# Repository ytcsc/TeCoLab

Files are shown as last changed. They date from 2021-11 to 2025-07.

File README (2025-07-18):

TeCoLab stands for Temperature Control Laboratory. It is an open source platform that contains (Arduino Nano compatible) hardware, firmware (Arduino Nano) and software (Python). The purpose of this project is to provide a cheap platform to help any interested person to understand several basic concepts about control systems. This project uses a MIT License, which means that you are basically free to do anything you like with this project.

All documentation has been moved to the (Wiki)[https://github.com/ytcsc/TeCoLab/wiki]!

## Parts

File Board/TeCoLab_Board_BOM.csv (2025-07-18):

Reference | Value | Footprint | Datasheet | Qty | DNP
A1 | Arduino_Nano_v3.x | Module:Arduino_Nano | http://www.mouser.com/pdfdocs/Gravitech_Arduino_Nano3_0.pdf | 1
C1 | 220uF x 25 V | Capacitor_THT:CP_Radial_D8.0mm_P3.50mm | ~ | 1
C2,C3,C4,C5 | 100nF | Capacitor_THT:C_Rect_L7.0mm_W2.0mm_P5.00mm | ~ | 4
D1,D2 | LED | LED_THT:LED_D3.0mm | ~ | 2
D3,D4 | 1N4007 | Diode_THT:D_DO-41_SOD81_P10.16mm_Horizontal | http://www.vishay.com/docs/88503/1n4001.pdf | 2
H1,H2,H3,H4,H5,H6,H7,H8 | Hole | MountingHole:MountingHole_3.2mm_M3,MountingHole:MountingHole_6mm | ~ | 8
J1 | Jack | Connector_BarrelJack:BarrelJack_Horizontal | ~ | 1
J2 | Supply_Terminal | TerminalBlock:TerminalBlock_bornier-2_P5.08mm | ~ | 1
J3 | DC Cooler | TerminalBlock:TerminalBlock_bornier-2_P5.08mm | ~ | 1
Q1 | BC337 | Package_TO_SOT_THT:TO-92_HandSolder | https://diotec.com/tl_files/diotec/files/pdf/datasheets/bc337.pdf | 1
Q2,Q3 | TIP122 | Package_TO_SOT_THT:TO-220-3_Vertical | http://www.fairchildsemi.com/ds/TI/TIP120.pdf | 2
R1,R2,R11,R13 | 1K | Resistor_THT:R_Axial_DIN0207_L6.3mm_D2.5mm_P7.62mm_Horizontal | ~ | 4
R3,R5,R7,R8 | 4.7K | Resistor_THT:R_Axial_DIN0207_L6.3mm_D2.5mm_P7.62mm_Horizontal | ~ | 4
R4,R9,R10 | 330R | Resistor_THT:R_Axial_DIN0207_L6.3mm_D2.5mm_P7.62mm_Horizontal | ~ | 3
R6,R12,R14 | 1K8 | Resistor_THT:R_Axial_DIN0207_L6.3mm_D2.5mm_P7.62mm_Horizontal | ~ | 3
R15,R16,R17,R18 | 10R / 5W | Resistor_THT:R_Axial_DIN0617_L17.0mm_D6.0mm_P20.32mm_Horizontal | ~ | 4
TP1,TP2,TP3,TP4,TP5,TP6,TP7,TP8 | TestPoint | TestPoint:TestPoint_THTPad_D1.0mm_Drill0.5mm | ~ | 8
U1,U3,U4 | DS18B20 | Package_TO_SOT_THT:TO-92_HandSolder | http://datasheets.maximintegrated.com/en/ds/DS18B20.pdf | 3
U2,U5,U6 | PC817 | Package_DIP:DIP-4_W7.62mm | http://www.soselectronic.cz/a_info/resource/d/pc817.pdf | 3

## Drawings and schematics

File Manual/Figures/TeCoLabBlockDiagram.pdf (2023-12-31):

## tecolab.py

# Arduino Nano

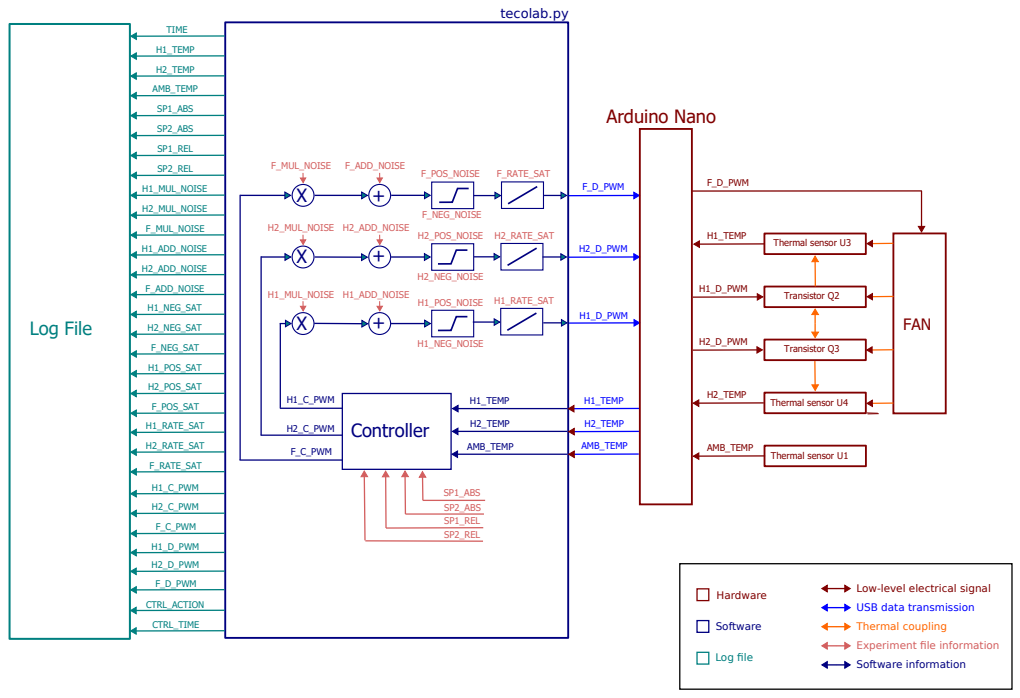
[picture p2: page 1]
H1_TEMP; H2_TEMP; AMB_TEMP; F_D_PWM; H2_D_PWM; H1_D_PWM; Thermal sensor U3; Transistor Q2; Transistor Q3; Thermal sensor U4; Thermal sensor U1; TIME; SP2_ABS; SP1_ABS; CTRL_ACTION; F_C_PWM; H2_C_PWM; H1_C_PWM; F_POS_SAT; H2_POS_SAT; H1_POS_SAT; F_NEG_SAT; H2_NEG_SAT; H1_NEG_SAT; F_ADD_NOISE; H2_ADD_NOISE; H1_ADD_NOISE; F_MUL_NOISE; H2_MUL_NOISE; H1_MUL_NOISE; SP2_REL; SP1_REL; H1_MUL_NOISE H1_ADD_NOISE H1_POS_NOISE; H1_NEG_NOISE; H2_MUL_NOISE H2_ADD_NOISE; H2_POS_NOISE; H2_NEG_NOISE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

Low-level electrical signal
USB data transmission
Thermal coupling
Experiment file information
Software information

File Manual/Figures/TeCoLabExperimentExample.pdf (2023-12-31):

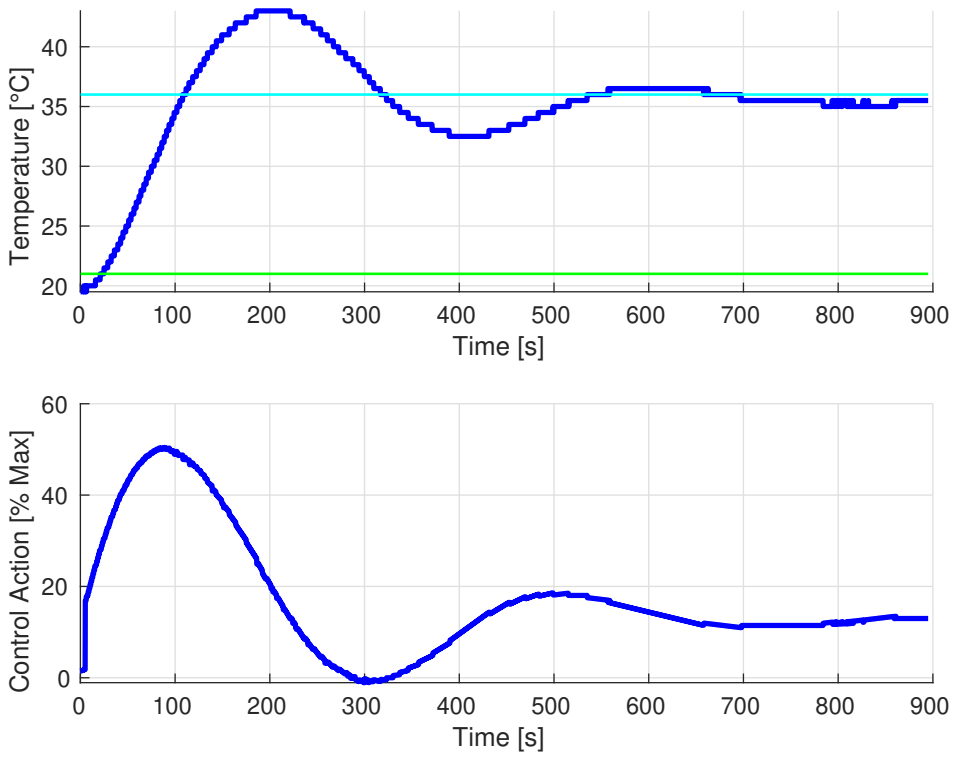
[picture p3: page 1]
Time [s]; Temperature [°C]

Control Action [% Max]

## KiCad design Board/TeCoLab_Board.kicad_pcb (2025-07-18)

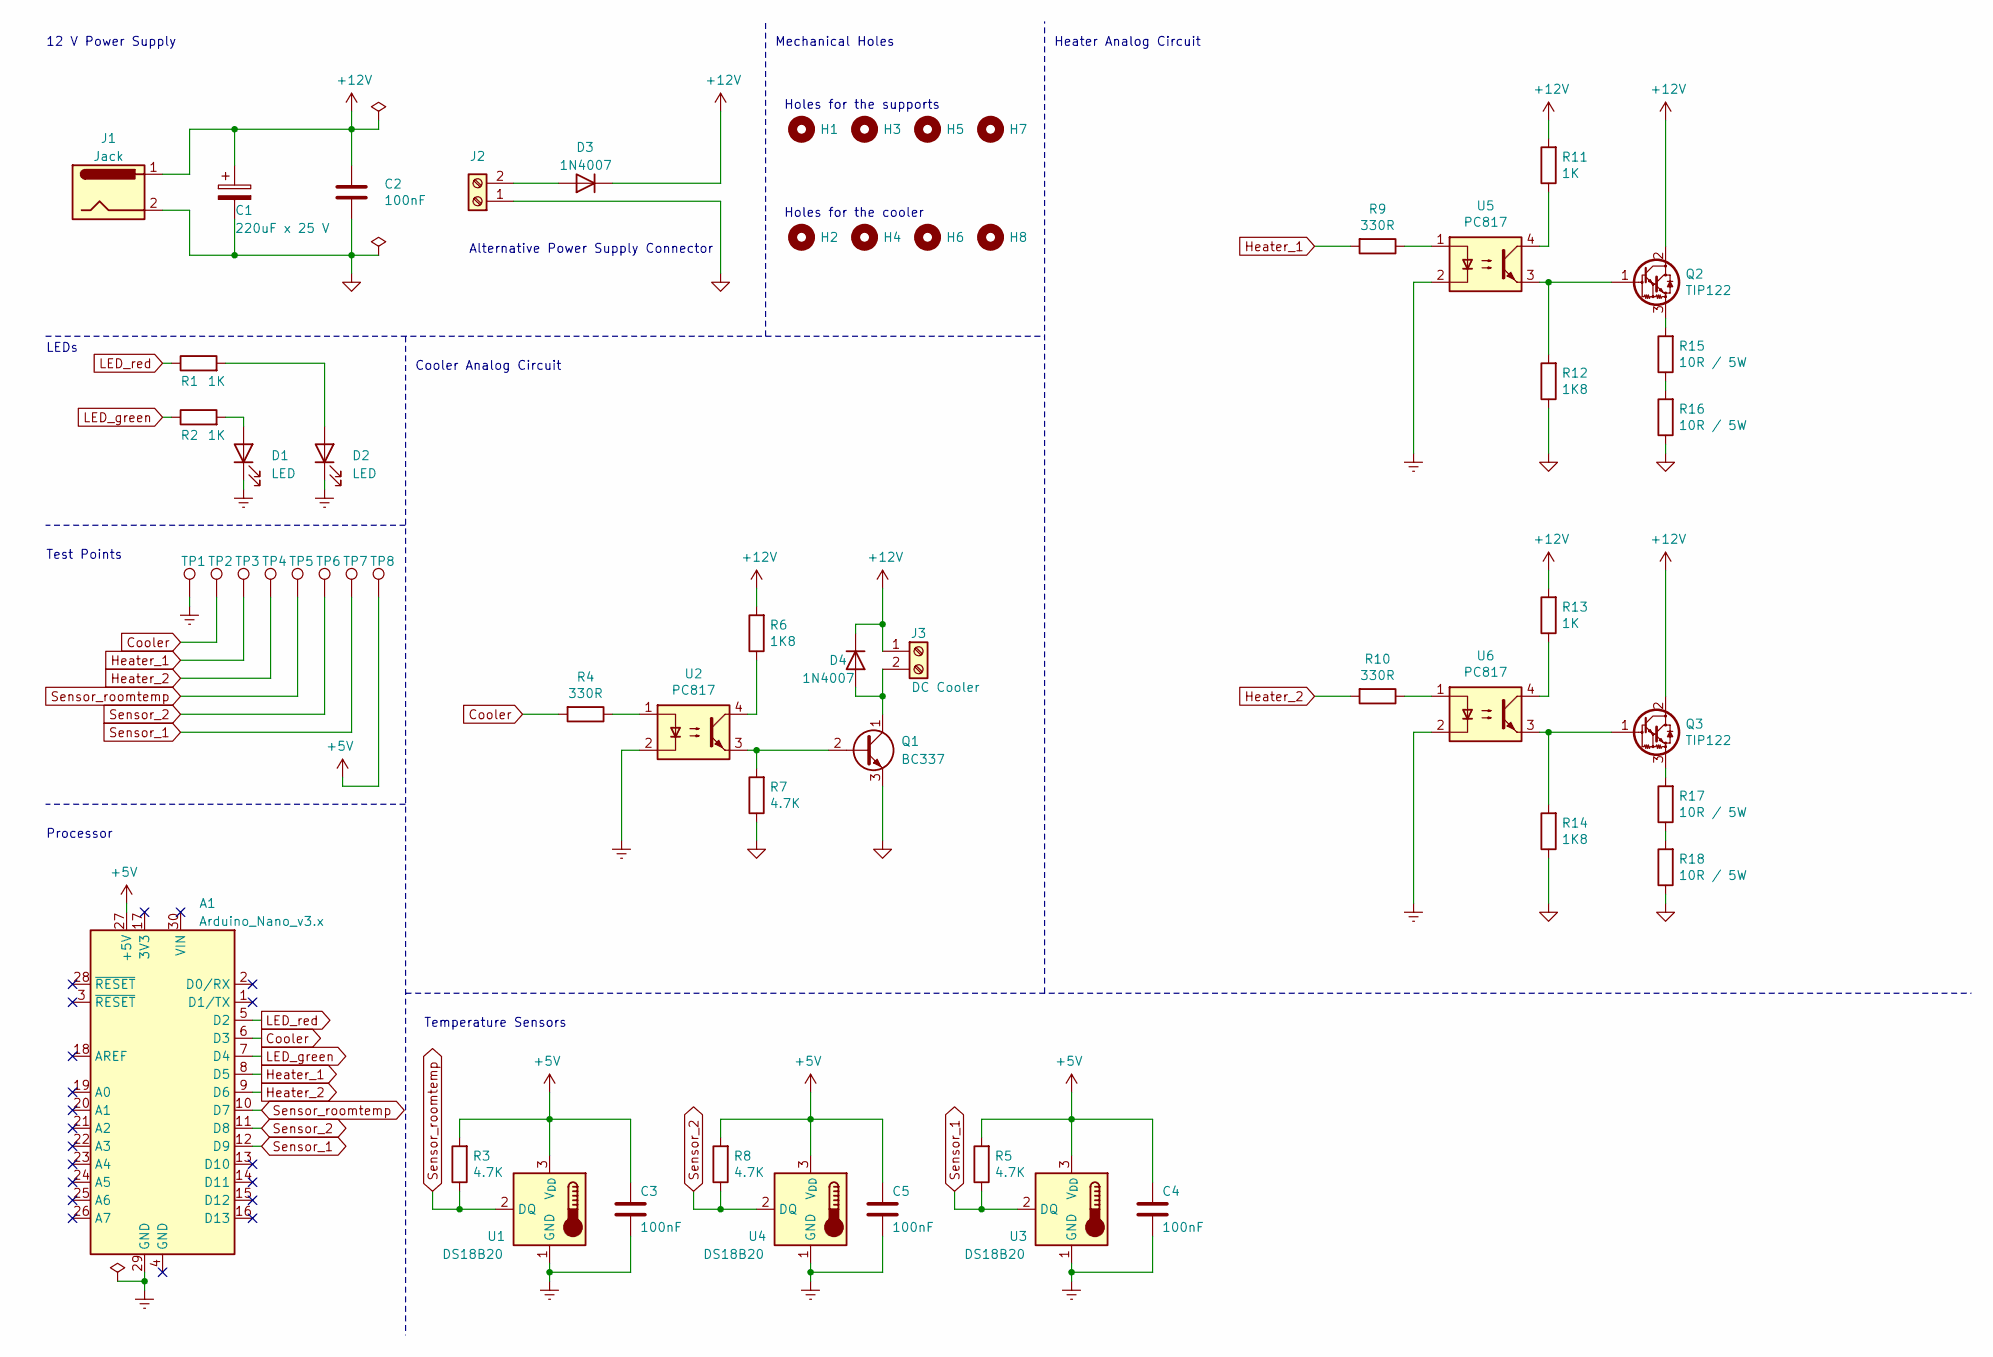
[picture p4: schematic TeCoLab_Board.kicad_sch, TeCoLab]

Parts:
A1: Arduino_Nano_v3.x; Arduino_Nano
C1: 220uF x 25 V; CP_Radial_D8.0mm_P3.50mm
C2, C3, C4, C5: 100nF; C_Rect_L7.0mm_W2.0mm_P5.00mm
D1, D2: LED; LED_D3.0mm
D3, D4: 1N4007; D_DO-41_SOD81_P10.16mm_Horizontal
H1, H3, H5, H7: Hole; MountingHole_6mm
H2, H4, H6, H8: Hole; MountingHole_3.2mm_M3
J1: Jack; BarrelJack_Horizontal
J2: Supply_Terminal; TerminalBlock_bornier-2_P5.08mm
J3: DC Cooler; TerminalBlock_bornier-2_P5.08mm
Q1: BC337; TO-92_HandSolder
Q2, Q3: TIP122; TO-220-3_Vertical
R1, R2, R11, R13: 1K; R_Axial_DIN0207_L6.3mm_D2.5mm_P7.62mm_Horizontal
R3, R5, R7, R8: 4.7K; R_Axial_DIN0207_L6.3mm_D2.5mm_P7.62mm_Horizontal
R4, R9, R10: 330R; R_Axial_DIN0207_L6.3mm_D2.5mm_P7.62mm_Horizontal
R6, R12, R14: 1K8; R_Axial_DIN0207_L6.3mm_D2.5mm_P7.62mm_Horizontal
R15, R16, R17, R18: 10R / 5W; R_Axial_DIN0617_L17.0mm_D6.0mm_P20.32mm_Horizontal
TP1, TP2, TP3, TP4, TP5, TP6, TP7, TP8: TestPoint; TestPoint_THTPad_D1.0mm_Drill0.5mm
U1, U3, U4: DS18B20; TO-92_HandSolder
U2, U5, U6: PC817; DIP-4_W7.62mm

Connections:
+5V: A1.27 (+5V), C3.1, C4.1, C5.1, R3.2, R5.2, R8.2, TP8.1, U1.3 (V_{DD}), U3.3 (V_{DD}), U4.3 (V_{DD})
+12V: C1.1, C2.1, D3.1 (K), D4.1 (K), J1.1, J3.1, Q2.2 (C), Q3.2 (C), R6.2, R11.2, R13.2
Cooler: A1.6 (D3), R4.2, TP2.1
GND: C1.2, C2.2, J1.2, J2.1, Q1.3 (E), R7.1, R12.1, R14.1, R16.1, R18.1
GNDREF: A1.29 (GND), C3.2, C4.2, C5.2, D1.1 (K), D2.1 (K), TP1.1, U1.1 (GND), U2.2, U3.1 (GND), U4.1 (GND), U5.2, U6.2
Heater_1: A1.8 (D5), R9.2, TP3.1
Heater_2: A1.9 (D6), R10.2, TP4.1
LED_green: A1.7 (D4), R2.1
LED_red: A1.5 (D2), R1.1
unnamed: D1.2 (A), R2.2
unnamed: D2.2 (A), R1.2
unnamed: D3.2 (A), J2.2
unnamed: D4.2 (A), J3.2, Q1.1 (C)
unnamed: Q1.2 (B), R7.2, U2.3
unnamed: Q2.1 (B), R12.2, U5.3
unnamed: Q2.3 (E), R15.2
unnamed: Q3.1 (B), R14.2, U6.3
unnamed: Q3.3 (E), R17.2
unnamed: R4.1, U2.1
unnamed: R6.1, U2.4
unnamed: R9.1, U5.1
unnamed: R10.1, U6.1
unnamed: R11.1, U5.4
unnamed: R13.1, U6.4
unnamed: R15.1, R16.2
unnamed: R17.1, R18.2
Sensor_1: A1.12 (D9), R5.1, TP7.1, U3.2 (DQ)
Sensor_2: A1.11 (D8), R8.1, TP6.1, U4.2 (DQ)
Sensor_roomtemp: A1.10 (D7), R3.1, TP5.1, U1.2 (DQ)

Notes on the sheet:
Holes for the cooler
12 V Power Supply
Alternative Power Supply Connector
Mechanical Holes
LEDs
Test Points
Processor
Heater Analog Circuit
Temperature Sensors
Holes for the supports
Cooler Analog Circuit

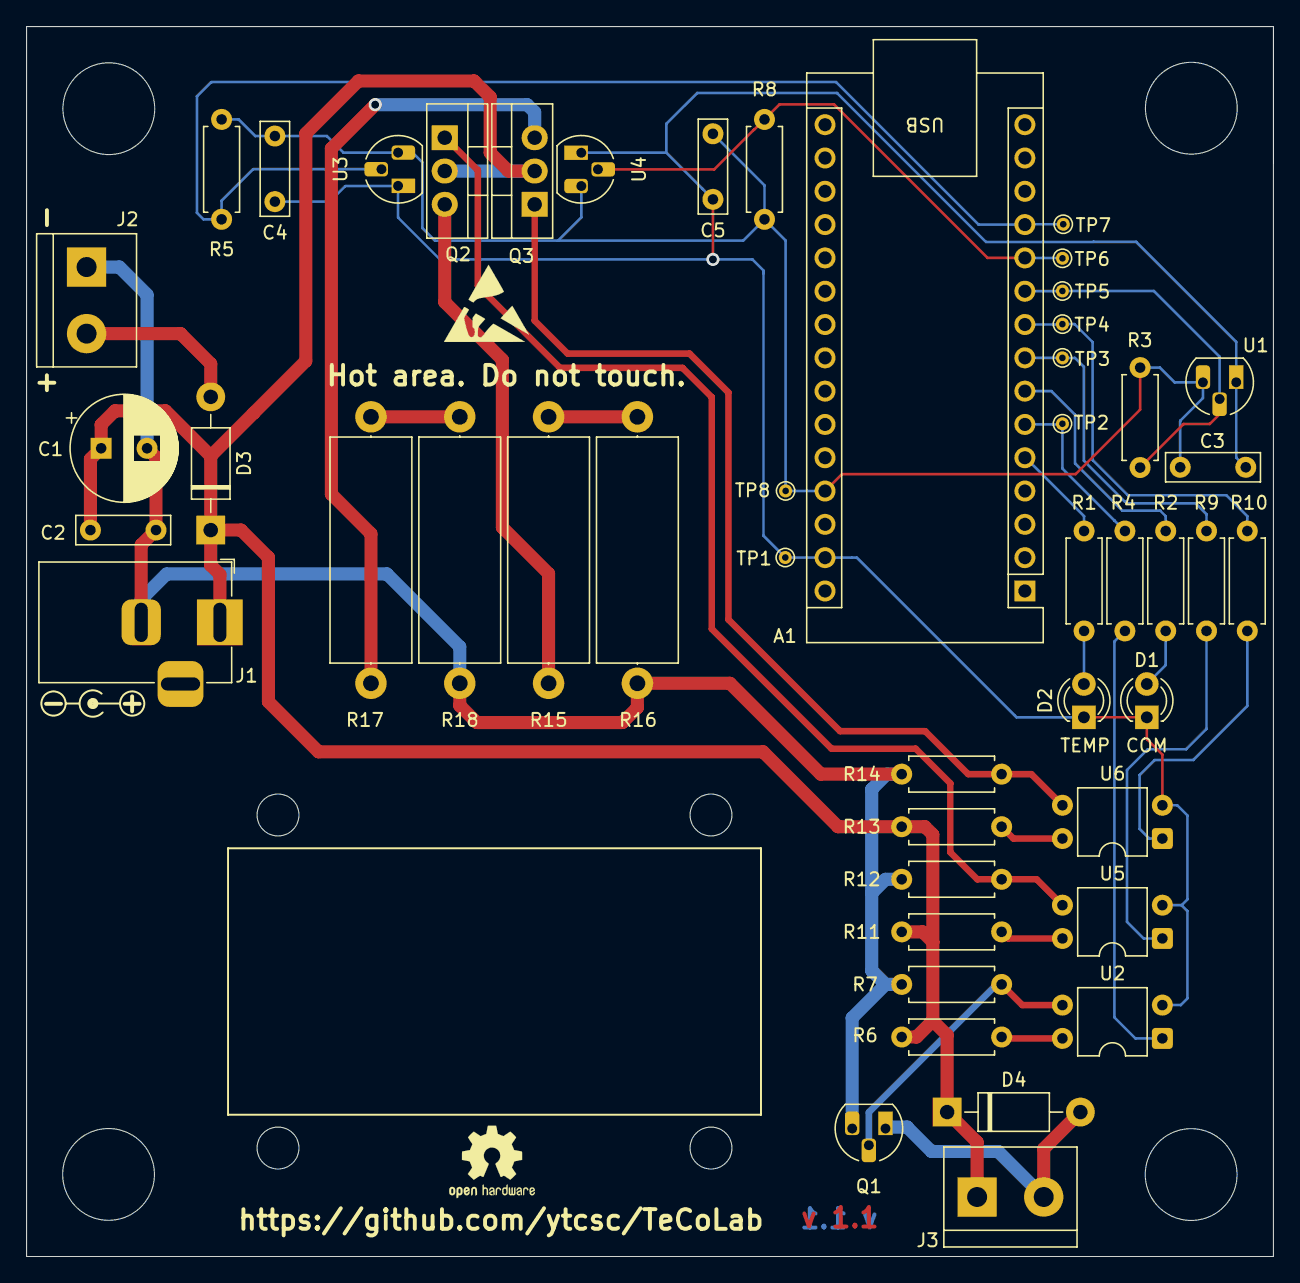
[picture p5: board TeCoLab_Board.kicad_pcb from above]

Board: 2 copper layers, 95.1 x 93.8 mm, 56 parts (0 on the bottom side), 29 nets.

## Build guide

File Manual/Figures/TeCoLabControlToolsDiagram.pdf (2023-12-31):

Modules.Utils

Controllers

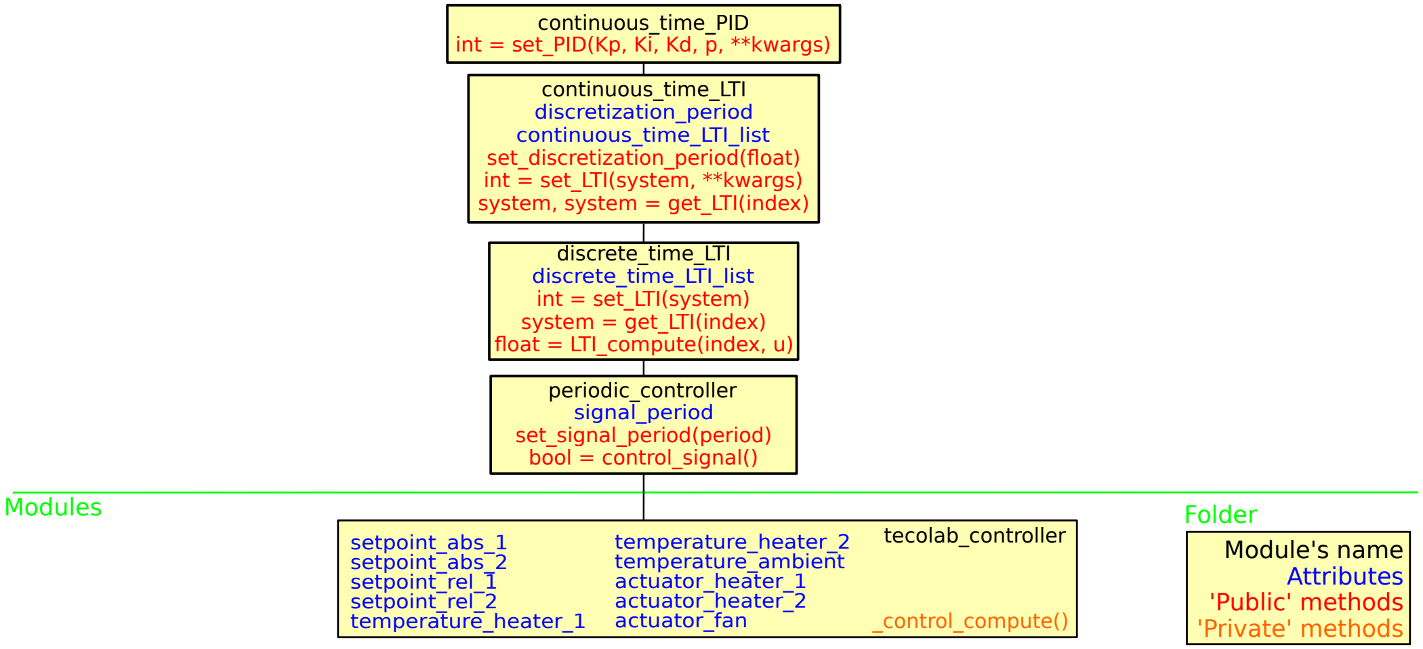
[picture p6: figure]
'Public' methods 'Private' methods; Attributes; tecolab_controller; Module's name; Folder; _control_compute(); setpoint_abs_1; Modules; setpoint_abs_2 setpoint_rel_1 setpoint_rel_2 temperature_heater_1; temperature_heater_2 temperature_ambient actuator_heater_1 actuator_heater_2 actuator_fan; periodic_controller; bool = control_signal(); signal_period; discrete_time_LTI; int = set_LTI(system); float = LTI_compute(index, u); continuous_time_LTI; int = set_LTI(system, **kwargs); discretization_period; continuous_time_PID int = set_PID(Kp, Ki, Kd, p, **kwargs); set_signal_period(period); system = get_LTI(index); discrete_time_LTI_list; continuous_time_LTI_list set_discretization_period(float); system, system = get_LTI(index)

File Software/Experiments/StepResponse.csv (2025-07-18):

TIME | SP1_ABS | SP2_ABS | SP1_REL | SP2_REL | H1_MUL_NOISE | H2_MUL_NOISE | F_MUL_NOISE | H1_ADD_NOISE | H2_ADD_NOISE | F_ADD_NOISE | H1_NEG_SAT | H2_NEG_SAT | F_NEG_SAT | H1_POS_SAT | H2_POS_SAT | F_POS_SAT | H1_RATE_SAT | H2_RATE_SAT | F_RATE_SAT
0 |  |  |  |  | 1 | 1 | 1 | 0 | 0 | 0 | 0 | 0 | 0 | 100 | 100 | 100 | 10000 | 10000 | 10000
10000 |  |  |  |  | 1 | 1 | 1 | 10 | 10 | 0 | 0 | 0 | 0 | 100 | 100 | 100 | 10000 | 10000 | 10000
1810000 | 0 | 0 | 0 | 0 | 0 | 0 | 0 | 0 | 0 | 0 | 0 | 0 | 0 | 0 | 0 | 0 | 0 | 0 | 0

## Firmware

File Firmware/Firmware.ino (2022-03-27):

/*
Copyright 2021 Leonardo Cabral

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
THE SOFTWARE IS PROVIDED "AS IS", WITHOUT WARRANTY OF ANY KIND, EXPRESS OR
IMPLIED, INCLUDING BUT NOT LIMITED TO THE WARRANTIES OF MERCHANTABILITY,
FITNESS FOR A PARTICULAR PURPOSE AND NONINFRINGEMENT. IN NO EVENT SHALL THE
AUTHORS OR COPYRIGHT HOLDERS BE LIABLE FOR ANY CLAIM, DAMAGES OR OTHER
LIABILITY, WHETHER IN AN ACTION OF CONTRACT, TORT OR OTHERWISE, ARISING FROM,
OUT OF OR IN CONNECTION WITH THE SOFTWARE OR THE USE OR OTHER DEALINGS IN THE
SOFTWARE.
*/

#include "tecolab.h"
//#include "communication.h"


TecolabDataStruct TecolabData;

OneWire roomTemperatureSensorBus(ROOMTEMPSENSOR_PIN);
OneWire heater1TemperatureSensorBus(HEATER1TEMPSENSOR_PIN);
OneWire heater2TemperatureSensorBus(HEATER2TEMPSENSOR_PIN);

DallasTemperature roomTempSensor(&roomTemperatureSensorBus);
DallasTemperature heater1TempSensor(&heater1TemperatureSensorBus);
DallasTemperature heater2TempSensor(&heater2TemperatureSensorBus);

void setup()
{
  Serial.begin(115200);
  Serial.setTimeout(3);
  while (Serial.available() > 0)
    Serial.read();
  
  roomTempSensor.begin();
  roomTempSensor.setResolution(SENSORRESOLUTION);
  roomTempSensor.setWaitForConversion(false);

  heater1TempSensor.begin();
  heater1TempSensor.setResolution(SENSORRESOLUTION);
  heater1TempSensor.setWaitForConversion(false);

  heater2TempSensor.begin();
  heater2TempSensor.setResolution(SENSORRESOLUTION);
  heater2TempSensor.setWaitForConversion(false);

  pinMode(LEDRED_PIN, OUTPUT);
  pinMode(COOLER_PIN, OUTPUT);
  pinMode(LEDGREEN_PIN, OUTPUT);
  pinMode(HEATER1_PIN, OUTPUT);
  pinMode(HEATER2_PIN, OUTPUT);

  digitalWrite(LEDRED_PIN, HIGH);
  digitalWrite(LEDGREEN_PIN, HIGH);
  delay(BLINK_TIME);
  digitalWrite(LEDRED_PIN, LOW);
  digitalWrite(LEDGREEN_PIN, LOW);
}

void loop()
{ 
  GetTemperatures();
  HardwareControl();
  CheckSerial();
}

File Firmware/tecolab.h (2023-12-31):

/*
Copyright 2021 Leonardo Cabral

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
THE SOFTWARE IS PROVIDED "AS IS", WITHOUT WARRANTY OF ANY KIND, EXPRESS OR
IMPLIED, INCLUDING BUT NOT LIMITED TO THE WARRANTIES OF MERCHANTABILITY,
FITNESS FOR A PARTICULAR PURPOSE AND NONINFRINGEMENT. IN NO EVENT SHALL THE
AUTHORS OR COPYRIGHT HOLDERS BE LIABLE FOR ANY CLAIM, DAMAGES OR OTHER
LIABILITY, WHETHER IN AN ACTION OF CONTRACT, TORT OR OTHERWISE, ARISING FROM,
OUT OF OR IN CONNECTION WITH THE SOFTWARE OR THE USE OR OTHER DEALINGS IN THE
SOFTWARE.
*/

#ifndef TECOLAB_H
#define TECOLAB_H

/* Libraries */
#include <Arduino.h>
#include <OneWire.h> 
#include <DallasTemperature.h>

/* Pins Definitions */
#define LEDRED_PIN 							2
#define COOLER_PIN 							3
#define LEDGREEN_PIN 						4
#define HEATER1_PIN 						5
#define HEATER2_PIN 						6
#define ROOMTEMPSENSOR_PIN			7
#define HEATER1TEMPSENSOR_PIN		9
#define HEATER2TEMPSENSOR_PIN		8

/* Addresses Definitions */
#define ROOMTEMP_LB_ADDR        0x00
#define ROOMTEMP_HB_ADDR        0x01
#define HEATER1TEMP_LB_ADDR     0x02
#define HEATER1TEMP_HB_ADDR     0x03
#define HEATER2TEMP_LB_ADDR     0x04
#define HEATER2TEMP_HB_ADDR     0x05
#define HEATER1PWM_ADDR         0x06
#define HEATER2PWM_ADDR         0x07
#define COOLERPWM_ADDR          0x08

/* Configurations */
#define BLINK_TIME 							250   // milliseconds
#define CONNECTION_TIME 				2000  // milliseconds
#define SENSORRESOLUTION 				9     // number of bits  
#define TEMPERATURECONVTIME  		100   // milliseconds (it depends on the resolution)
#define OVERHEATTEMPERATURE     100   // degrees Celsius
#define HIGHTEMPERATURE         50    // degrees Celsius

/* Status Definitions */
#define TSTATUS_LOWTEMP         0
#define TSTATUS_HIGHTEMP        1
#define TSTATUS_OVERHEATED      2
#define CSTATUS_WAITING					0
#define CSTATUS_CONNECTED				1

/* TeCoLab data struct */
struct TecolabDataStruct
{
	short roomTemp;
	short heater1Temp;
	short heater2Temp;
	byte heater1PWM;
	byte heater2PWM;
	byte coolerPWM;
	byte connectionStatus;
  byte temperatureStatus;
	unsigned long lastConversionTime;
	unsigned long lastCommunicationTime;
};

/* TeCoLab functions */
void GetTemperatures(void);
void HardwareControl(void);
void CheckSerial(void);
byte getValue(byte);
void setValue(byte, byte);

/* External variables */
extern TecolabDataStruct TecolabData;
extern OneWire roomTemperatureSensorBus;
extern OneWire heater1TemperatureSensorBus;
extern OneWire heater2TemperatureSensorBus;
extern DallasTemperature roomTempSensor;
extern DallasTemperature heater1TempSensor;
extern DallasTemperature heater2TempSensor;

#endif

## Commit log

2021-10-30 Add files via upload
    Electronic schematic added
    [TeCoLab_Board.kicad_pcb, TeCoLab_Board.sch]
2021-10-30 Added english text in the schematic.
    [TeCoLab_Board.sch]
2021-10-30 Associated footprints and generated BOM.
    [TeCoLab_Board.sch, TeCoLab_Board_BOM.csv]
2021-11-14 Changed some resistor's values due to excessive power dissipation.
    [TeCoLab_Board.sch]
2021-11-21 Schematic changes. Arduino NANO replaced Arduino UNO. Alternative power supply connector added. Mechanical holes added. TIP122 replaced discrete darlington pair. 100nF capacitors inserted in the powe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
    [TeCoLab_Board.sch]
2021-11-29 Schematic: added testpoints; the analog circuits were simplified; the cooler connector was changed. Firmware: first commit.
2021-12-11 Schematic: small changes to help the PCB design. PCB design: first commit. Corrections in the previous commit, since some files were not added.
    [TeCoLab_Board.kicad_pcb, TeCoLab_Board.sch, TeCoLab_Board_BOM.csv]
2022-01-14 PCB design: PCB size reduction.
    [TeCoLab_Board.kicad_pcb]
2022-01-22 PCB design: Final modifications before PCB manufacturing. The polarity of the DC Jack was changed since DC power supplies often have the positive terminal in the middle.
    [TeCoLab_Board.kicad_pcb, TeCoLab_Board.sch, TeCoLab_Board_BOM.csv]
2022-01-27 PCB design: added PCB version on it.
    [TeCoLab_Board.kicad_pcb]
2022-01-27 PCB: Gerbers added.
    [TeCoLab_Board-B_Cu.gbl, TeCoLab_Board-B_Mask.gbs, TeCoLab_Board-B_SilkS.gbo, TeCoLab_Board-Edge_Cuts.gm1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]
2022-03-27 Firmware: Increased Baudrate from 9600 to 115200 to enhance performance.
    [TeCoLab_Board.kicad_pcb]
2022-04-02 PCB: Mounting holes updated to 7 mm. TeCoLab logo resized to 70 percent of the previous size.
    [TeCoLab_Board.kicad_pcb]
2022-05-23 Software: Added step response experiment and Octave script to analyse this experiment.
    [StepResponse.csv]
2023-12-31 Main Branch Major Update (#12)
    * columns name modified
    * Update README
    Substituted Arduino UNO with Arduino NANO, as the latter board was employed during the development.
    * FIle directory changed
    * Schematic: swap of the two labels named Sensor1 and Sensor2. This changes nothing in the PCB layout, but the files were checked as well and saved, generating a new version of them too. Firmware: ch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
    * Feat/step response identification (#8)
    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
    [StepResponse.csv, TeCoLab_Board-B_Cu.gbl, TeCoLab_Board-B_Mask.gbs, TeCoLab_Board-B_SilkS.gbo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]
2023-12-31 Main Branch Major Update (Correction) (#13)
    * step response script
    * remove useless code in step response script
    * step_response_identification fixed
    * Update st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
2023-12-31 Main Branch Major Update (Correction) (#14)
    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
2025-07-07 Fix incorrect condition logic for low-temperature status detection (#17) (#18)
2025-07-18 Main Branch Major Update (#19)
    * Hardware: Update files to comply with KiCad version 8.0.
    * Software: Update dependency handling and experiment logging
    - Added requirements.txt for managing Python dependencies
    - Updated Manual.tex and Manual.pdf to reflect new setup instructions
    - Modified tecolab_experiment.py to handle future pandas concat behavior
    - Added rate saturation fields to StepResponse.csv header
    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
    [StepResponse.csv, TeCoLab_Board-B_Cu.gbl, TeCoLab_Board-B_Mask.gbs, TeCoLab_Board-B_SilkS.gbo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]
